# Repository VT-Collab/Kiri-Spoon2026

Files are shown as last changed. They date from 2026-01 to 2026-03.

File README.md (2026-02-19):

# Kiri-Spoon: A Kirigami Utensil for Robot-Assisted Feeding

Kiri-Spoon: A Kirigami Utensil for Robot-Assisted Feeding

There are three folders: Handheld Kirispoon, Robotic Kirispoon End-Effector, and Ansys Model

There are prt, zip, step, and md files in the Handheld Kirispoon and Robotic End-Effector folders

md files provide instructions for Kirispoon reproduction

Download the zip file for the assembly and all necessary files

Individual prt files are located in the folders

The same kirigami sheet is located in multiple folders

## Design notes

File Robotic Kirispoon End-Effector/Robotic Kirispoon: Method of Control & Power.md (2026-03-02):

# **Robotic Kirispoon: Method of Control & Power**

## Description
There are multiple ways to control and power the Robotic Kirispoon. This document gives the two examples of control that were utilized in research. This document includes materials, tools, and instructions to reproduce these methods of control. An order form is located at the end of each method. 

## Method 1: Control through the use of a button
This method involves wiring the robotic kirispoon to an adaptable power source, an arduino, and a button to open and close the end-effector. This can be useful when providing an easy interface for users.

### Parts
    - Power Adapter 7 volts
    - Push Button
    - Four 10K Ohm Resistors 
    - Robotic Kirispoon End-effector (Servo Motor)
    - Arduino
    - Arduino Cable (This is used to connect the Arduino to the computer)
    - 9 Male/Male Wires
    - DC barrel jack adapter (Enables the power supply to connect to the Servo Motor)
    - Half Breadboard

### Files
    - KiriButton.ino 

## Instructions



    1. Build the circuit shown above
        *Note: Pay attention to the specific pins on the Arduino and the specific wire colors on the Servo Motor
        *Note: The Servo Motor is a part of the Robotic Kirispoon End-effector
    2. Download the following files:
        *Kiributton.ino
    3. Connect the Arduino to the computer with the above file
    4. In the Arduino IDE, open the Kiributton.ino sketch
    5. Upload the sketch to the Arduino to run the code
    6. Turn on the power supply to the motor
    7. Pressing the button will move the motor to open and close the Robotic Kirispoon, completing method 1

## Order List for Method 1
There are multiple ways to make the circuit shown in Method 1. The parts list below will contain the items to make the circuit utilized during research. A picture of that circuit is included below. 
(Note: each resistor shown in the circuit diagram is 10k ohms)
ResearchCircuitArduino

Before clicking on the links in this list, there are a couple of important things to note:
    - Note: The Arduino Cable is for a USB type B, depending on the computer used, another cable may need to be selected
    - Note: This list assumes the Robotic Kirispoon is already built
    - Note: The left-most column shows the number of the units to order
    - Note: This list will yield more materials than necessary to build the circuit
    - Note: This list assumes that a printer is readily available
    - Note: The “Link Cost” column shows the price of the product in the link address when this document was made, 
            NOT the cost for the amount of material needed for one spoon

|# of Units|Part/Material|Unit Cost|
|---|---|---|
|1|[Arduino](https://store-usa.arduino.cc/products/arduino-uno-rev3?utm_source=google&utm_medium=cpc&utm_campaign=US-Pmax&gad_source=1&gad_campaignid=21317508903&gbraid=0AAAAACbEa84vFf-vMm0bSp7Ru9_hjazM2&gclid=CjwKCAiAmp3LBhAkEiwAJM2JUPkOYBex2DY1xz7MZbzy9ACP6xAJaNXNZbybs5sxCYbR4J5JAEu0iBoCLawQAvD_BwE )|$27.60|
|1|[Arduino Cable](https://store-usa.arduino.cc/collections/cables-wires/products/usb-2-0-cable-type-ab#looxReviews )|$6.50|
|1|[Power Adapter 7 volts  (includes a DC barrel jack adapter)](https://www.amazon.com/dp/B0B5GFJNS2/ref=sspa_dk_detail_3?psc=1&pd_rd_i=B0B5GFJNS2&pd_rd_w=mGGio&content-id=amzn1.sym.386c274b-4bfe-4421-9052-a1a56db557ab&pf_rd_p=386c274b-4bfe-4421-9052-a1a56db557ab&pf_rd_r=2W6D7QCPWHGRAN1Y680W&pd_rd_wg=op3lr&pd_rd_r=806a2af1-b4f9-48da-8165-049daf2cf8ef&sp_csd=d2lkZ2V0TmFtZT1zcF9kZXRhaWxfdGhlbWF0aWM )|$17.99|
|1|[10k Ohm Resistors (10 pack)](https://www.amazon.com/California-JOS-Carbon-Resistor-Tolerance/dp/B0BR68QQPF/ref=sr_1_3?dib=eyJ2IjoiMSJ9.CitfKyPFE5pIWUVS7QgFNKXsj0QNgNypSwtNjBlsotvRwHn9qigSDCFk9SjCPPLbGNeCPsj8pLYMNuQCzHIqfW5iafJLYPsvQ9Wtt7kOpD-ID9ATt-K7_nxSs8aBtOSvzfdjrLO01KDsecxBB8ocr0xEixn1dCMHj_CFr7BhUZ6v7vj1YpLuwfVmYQP2TTMp7lnIaGpZYiojs9D-rkrHKbrX4pLbe8gkUY-w42ecziI.BQNyUV8xU7tfTQWOo8j2iS77g3V_r7tXK5orqj6SgIE&dib_tag=se&hvadid=792677910694&hvdev=c&hvexpln=67&hvlocphy=9197701&hvnetw=g&hvocijid=18200258952104306485--&hvqmt=e&hvrand=18200258952104306485&hvtargid=kwd-6783760661&hydadcr=2794_13896043&keywords=10k%2Bohm%2Bresistor&mcid=4133edb7e5523276b60c85ef7beef09d&qid=1768418028&sr=8-3&th=1)|$3.99|
|1|[Half Breadboard](https://www.digikey.com/en/products/detail/dfrobot/FIT0096/7597069?gclsrc=aw.ds&gad_source=1&gad_campaignid=20232005509&gbraid=0AAAAADrbLliWzviSy71Vuvh3rn68vr0yy&gclid=CjwKCAiAmp3LBhAkEiwAJM2JUAsJKqjgIozuQ8PYXdKIrhqhSSRvO_wl6e72EOud3CsVuHPRZbkJcBoCjGIQAvD_BwE )|$2.90|
|1|[Push button (does not need an adapter)](https://www.amazon.com/EG-STARTS-Buttons-Illuminated-Machine/dp/B01LZMANZ7#:~:text=Wiring%20Information:,No%20lock%20button%20switch. )|$11.99|
|1|[M/M Wires (20 Count)](https://www.digikey.com/en/products/detail/sparkfun-electronics/PRT-12795/5993860)|$2.95|
||Total Cost: |$73.92|

## Method 2: Control through the use of Serial Messages
This method involves wiring the Robotic Kirispoon to an adaptable power source and Arduino. Serial messages will be received by the Arduino to open and close the end-effector. Researchers utilized VS Code to send Serial messages; an example is included. This can be useful when combining the open and close capability of the robotic Kirispoon with controls for other machines. An example of this would be using a controller to control the Robotic Kirispoon and the robot arm it is attached to.

### Parts
    - Power Adapter 7 volts
    - Robotic Kirispoon End-effector (Servo Motor)
    - Arduino
    - Arduino Cable (This is used to connect the Arduino to the computer)
    - 3 Male/Male Wires
    - Breadboard

### Files
    - Endeffector_Control_Example.ino
    - Open_close_Kirispoon.py

### Instructions


    1. Build the circuit shown above
        *Note: Pay attention to the specific pins on the Arduino and the specific wires on the Servo Motor
    2. Download the following files
        - Endeffector_Control_Example.ino
    3. Connect the Arduino to the computer with the above file
    4. In the Arduino IDE, open the Endeffector_Control_Example.ino sketch
    5. Upload the sketch to the Arduino to run the code
    6. Turn on the power supply to the motor
    7. In another software, such as Visual Studio, controlling the Robotic Kirispoon can be done by sending 
        the specific messages over the Arduino Cable, which correspond to the action in the Arduino code. 
        An example of sending serial messages in VS Code is seen in the Open_close_Kirispoon.py and below. 


    To run the example shown above, follow the steps below:
    1. Download the following:
        - Open_close_Kirispoon.py
    2. Open the file above in VS Code
    3. Go into the folder containing Open_close_Kirispoon.py
    4. Right click on any white space in the folder to open a menu
    5. Choose “Open in Terminal”
    6. Make sure all the dependencies in requirements.txt are downloaded
    7. Type the following in your terminal: 
        python Open_close_Kirispoon.py
    8. Press the "enter" key

## Order List for Method 2
There are multiple ways to make the circuit shown in Method 2. The parts list below will contain the items to make the circuit utilized during research. This circuit is similar to the one featured in the order form above, except that the orange and green wires, the button, and the resistors have been removed. A computer capable of sending serial messages corresponding to the Arduino is assumed to be available. 

Before clicking on the links in this list, there are a couple of important things to note:

    - Note: The Arduino Cable is for a USB type B. Depending on the computer used, another cable may need to be selected
    - Note: This list assumes the Robotic Kirispoon is already built
    - Note: The left-most column shows the number of the material to order
    - Note: This list will yield more materials than necessary to build the circuit
    - Note: This list assumes that a printer is readily available
    - Note: This list assumes that a computer or other hardware device capable of sending serial messages is readily available
    - Note: The “Link Cost” column shows the price of the product in the link address when this document was made, 
            NOT the cost for the amount of material needed for one spoon

|# of Units|Part/Material|Unit Cost|
|---|---|---|
|1|[Arduino](https://store-usa.arduino.cc/products/arduino-uno-rev3?utm_source=google&utm_medium=cpc&utm_campaign=US-Pmax&gad_source=1&gad_campaignid=21317508903&gbraid=0AAAAACbEa84vFf-vMm0bSp7Ru9_hjazM2&gclid=CjwKCAiAmp3LBhAkEiwAJM2JUPkOYBex2DY1xz7MZbzy9ACP6xAJaNXNZbybs5sxCYbR4J5JAEu0iBoCLawQAvD_BwE )|$27.60|
|1|[Arduino Cable](https://store-usa.arduino.cc/collections/cables-wires/products/usb-2-0-cable-type-ab#looxReviews )|$6.50|
|1|[Power Adapter 7 volts (includes a DC barrel jack adapter)](https://www.amazon.com/dp/B0B5GFJNS2/ref=sspa_dk_detail_3?psc=1&pd_rd_i=B0B5GFJNS2&pd_rd_w=mGGio&content-id=amzn1.sym.386c274b-4bfe-4421-9052-a1a56db557ab&pf_rd_p=386c274b-4bfe-4421-9052-a1a56db557ab&pf_rd_r=2W6D7QCPWHGRAN1Y680W&pd_rd_wg=op3lr&pd_rd_r=806a2af1-b4f9-48da-8165-049daf2cf8ef&sp_csd=d2lkZ2V0TmFtZT1zcF9kZXRhaWxfdGhlbWF0aWM )|$17.99|
|1|[Half Breadboard](https://www.digikey.com/en/products/detail/dfrobot/FIT0096/7597069?gclsrc=aw.ds&gad_source=1&gad_campaignid=20232005509&gbraid=0AAAAADrbLliWzviSy71Vuvh3rn68vr0yy&gclid=CjwKCAiAmp3LBhAkEiwAJM2JUAsJKqjgIozuQ8PYXdKIrhqhSSRvO_wl6e72EOud3CsVuHPRZbkJcBoCjGIQAvD_BwE )|$2.90|
|1|[M/M Wires (20 Count)](https://www.digikey.com/en/products/detail/sparkfun-electronics/PRT-12795/5993860 )|$2.95|
||Total Cost: |$57.94|

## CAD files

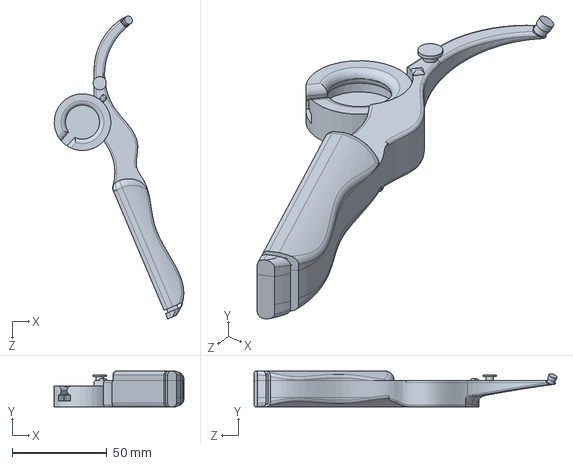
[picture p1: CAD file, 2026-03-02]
Handheld Kirispoon/Part Files/RightHandle.SLDPRT
68.5 x 19.0 x 160.1 mm

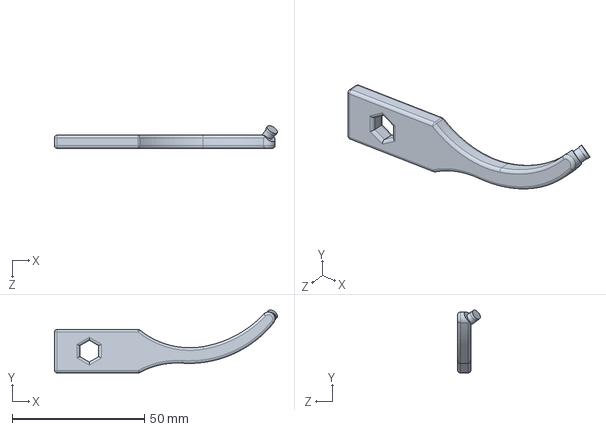
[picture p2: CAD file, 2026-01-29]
Robotic Kirispoon End-Effector/Part Files/Angled_Kiripost_45Right.SLDPRT
84.4 x 23.8 x 8.60 mm

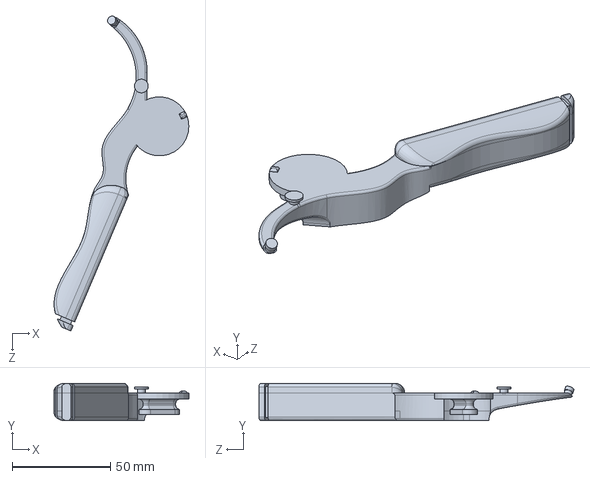
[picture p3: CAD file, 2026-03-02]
Handheld Kirispoon/Part Files/LeftHandle.SLDPRT
68.5 x 19.0 x 160.1 mm

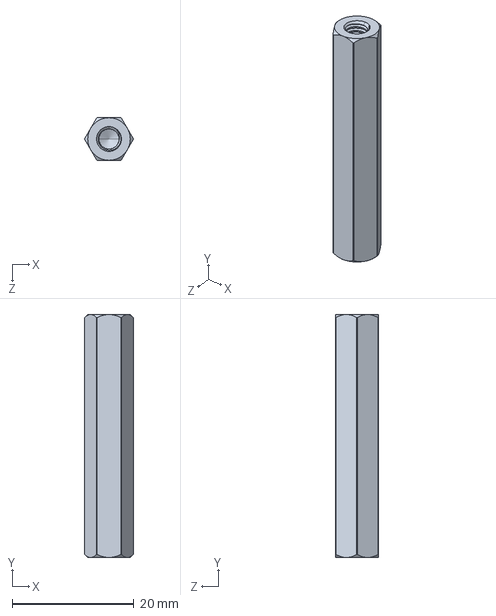
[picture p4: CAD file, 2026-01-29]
Robotic Kirispoon End-Effector/Part Files/HexShaft.SLDPRT
8.00 x 40.0 x 7.00 mm

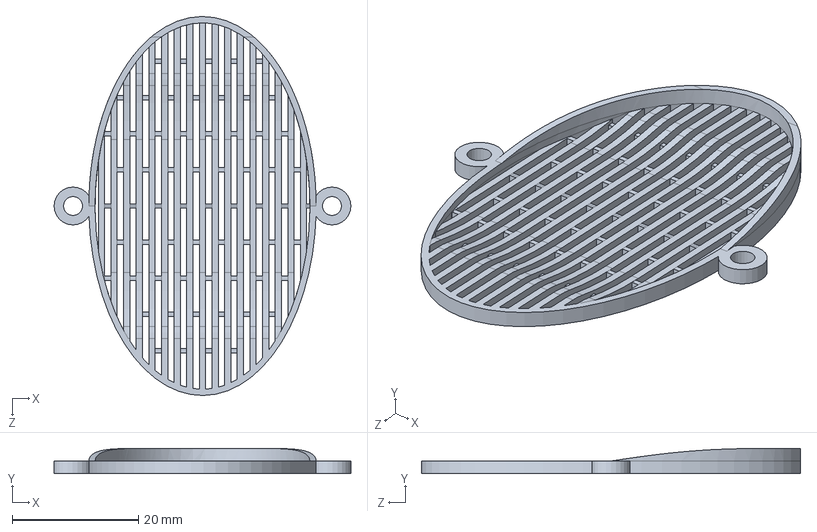
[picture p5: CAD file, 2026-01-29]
Handheld Kirispoon/Part Files/KirigamiMesh.SLDPRT
47.0 x 4.00 x 60.0 mm

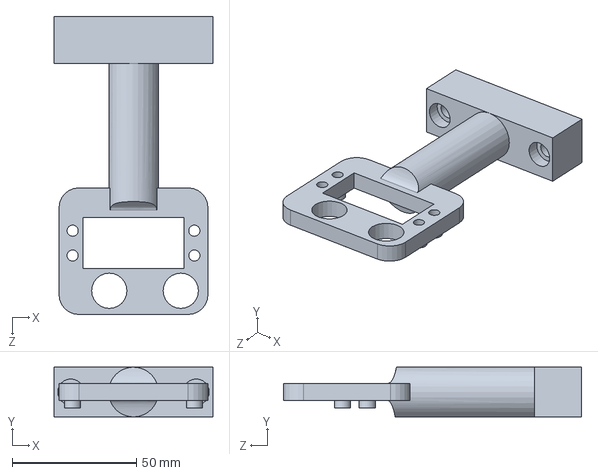
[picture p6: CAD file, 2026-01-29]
Robotic Kirispoon End-Effector/Part Files/PandaHousingOneServo.SLDPRT
64.0 x 20.0 x 120.0 mm

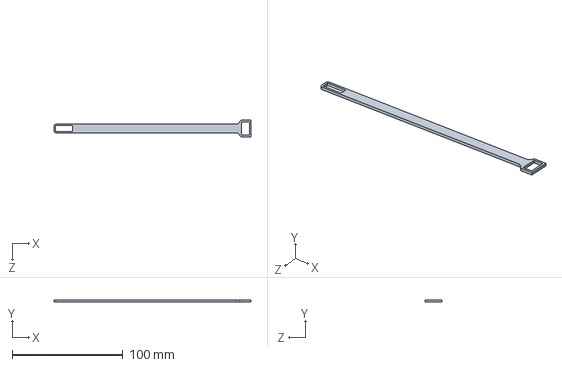
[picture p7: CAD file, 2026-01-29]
Handheld Kirispoon/Part Files/GoodieStrap.SLDPRT
178.0 x 2.00 x 15.0 mm

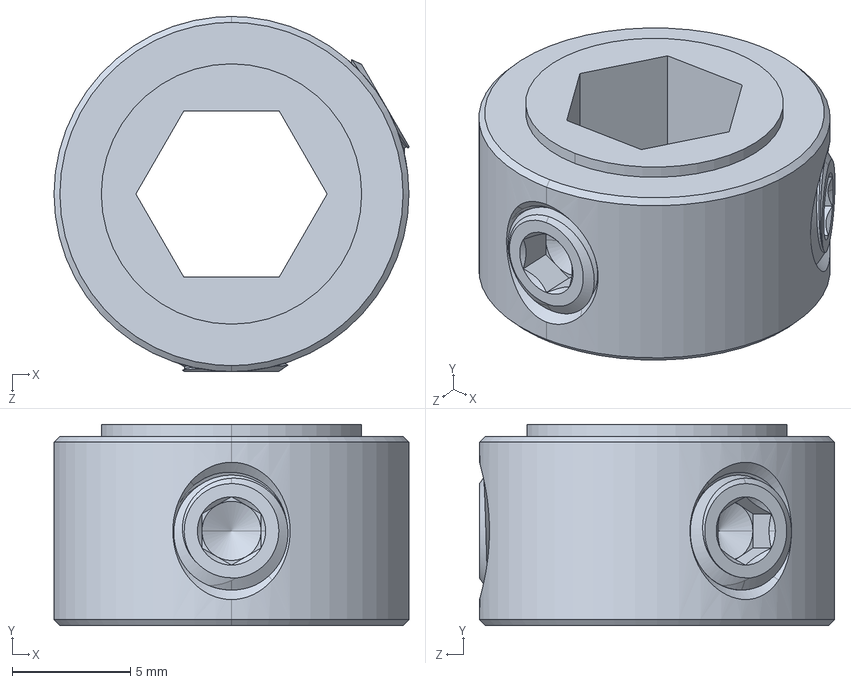
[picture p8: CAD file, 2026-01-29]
Robotic Kirispoon End-Effector/Part Files/HexCollar.SLDPRT
15.0 x 8.50 x 15.0 mm

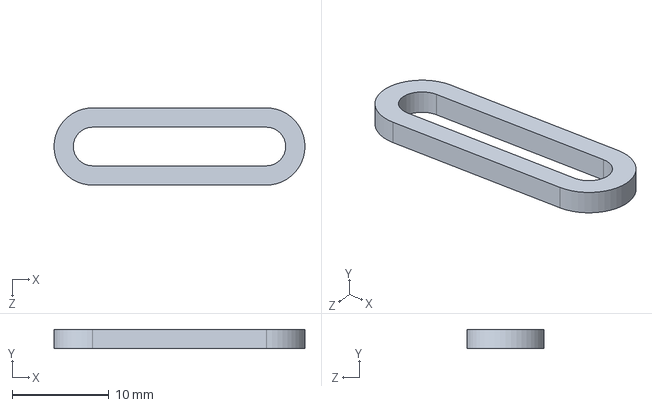
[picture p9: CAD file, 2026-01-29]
Handheld Kirispoon/Part Files/TPU Band.SLDPRT
26.0 x 2.00 x 8.00 mm

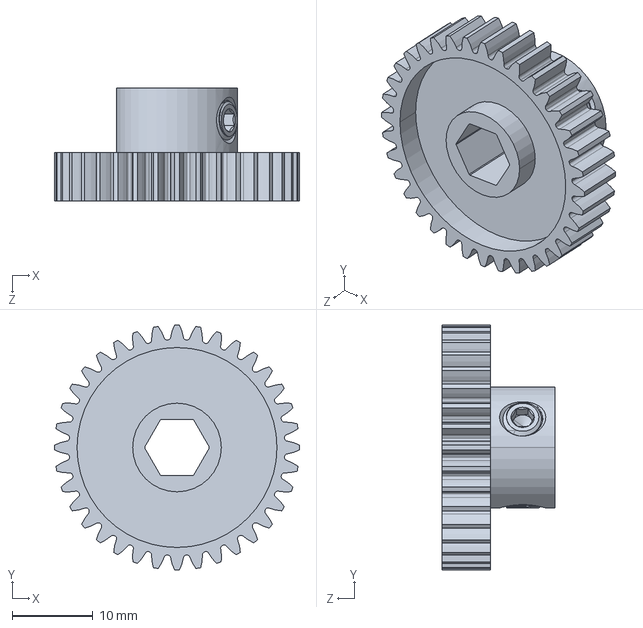
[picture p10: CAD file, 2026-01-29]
Robotic Kirispoon End-Effector/Part Files/HexGear36T.SLDPRT
30.4 x 30.4 x 14.0 mm

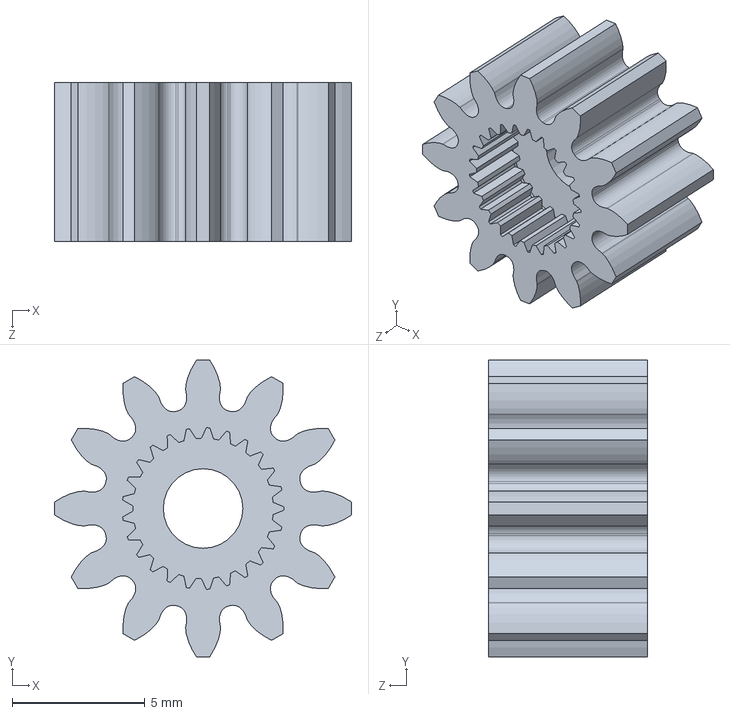
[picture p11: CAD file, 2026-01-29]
Robotic Kirispoon End-Effector/Part Files/ServoGear.SLDPRT
11.2 x 11.2 x 6.00 mm

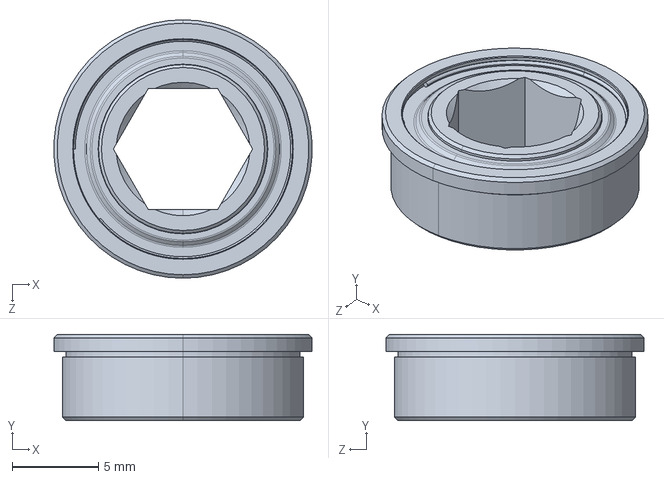
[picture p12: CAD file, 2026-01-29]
Robotic Kirispoon End-Effector/Part Files/HexBearing.SLDPRT
15.0 x 5.00 x 15.0 mm

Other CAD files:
Robotic Kirispoon End-Effector/Part Files/Angled_Kiripost_45Left.SLDPRT
Handheld Kirispoon/STL Files/GoodieStrap.STL
Handheld Kirispoon/STL Files/KirigamiMesh.STL
Handheld Kirispoon/STL Files/LeftHandle.STL
Handheld Kirispoon/STL Files/RightHandle.STL
Handheld Kirispoon/STL Files/TPU Band.STL
Robotic Kirispoon End-Effector/STL Files/KirigamiMesh.STL
Robotic Kirispoon End-Effector/STL Files/PandaHousingOneServo.STL

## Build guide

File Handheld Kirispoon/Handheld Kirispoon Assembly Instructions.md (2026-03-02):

# **Handheld Kirispoon Assembly Instructions**

## Description

The Handheld Kirispoon is a 3D-printed assistive device that functions by encompassing food with a flexible mesh. This document includes materials, tools, and instructions to reproduce the device. An order form is located at the end of this document.

### Materials
- PLA 3D-printing filament (35 grams)
- TPU (85A) 3D-printing filament (8 grams)

### Tools
- 3D printer
- Pliers (See Note in Step 2)

### Files
- LeftHandle.STL
- RightHandle.STL
- TPU Band.STL
- KirigamiMesh.STL
- GoodieStrap.STL (Optional)

## Instructions

#### 1. Download the following .STL files:
    - LeftHandle.STL
    - RightHandle.STL
#### 2. Print PLA parts

    1. On a 3D printing software, import the two files downloaded in step 1
    
handlesOnPrinterBed
    
    2. Orient the two files onto the printer bed as shown above
    3. Adjust the printer settings to allow PLA printing
    4. Load PLA filament into the 3D printer
    5. Upload and print the two PLA parts
    6. Take the two parts off and remove the supports
        *A small pair of pliers makes removing the supports easier
#### 3. Download the following .STL files:
    - TPU Band.STL
    - KirigamiMesh.STL
    - GoodieStrap.STL (Optional)
#### 4. Print TPU parts
    1. On a 3D printing software, import the files downloaded in step 3



    2. Orient the files onto the printer bed as shown above
    3. Adjust the printer settings to allow TPU printing
        *Note: Some printers have trouble printing TPU. Look up the best parameters for printing TPU filament on your printer.
    4. Load TPU filament into the 3D printer
    5. Upload and print the TPU parts
#### 5. Assemble



    1. Connect the two handles by aligning the two bumps located in circles in Figure (a). Imagine a line between the two bumps. 
        Orient that line so it passes through the opening in the right handle. Slide the bumps toward each other in a straight line 
        so that the left handle slides into the right handle. The handles should now rotate while staying connected, similar to 
        a pair of pliers
    2. Take the kirigami sheet and locate the two circular holes on the side. Orient the kirigami sheet so that the thicker part 
        is closer to the handles. Attach the circular holes of the kirigami sheet to the pegs on the end of the handles. 
        These pegs can be seen in the red circles of Figure (b). The attachment will be a tight fit, but this will ensure that 
        the kirigami sheet is snug on the handles. At this point, squeezing the handles will stretch the kirigami sheet. 
    3. Wrap the TPU band around the two remaining pegs. These pegs are in the red circles of Figure (c). The band helps the handles 
        spring back by adding some resistance to the handles when they are squeezed. 
    4. There should now be a fully assembled Kirispoon similar to this one shown in Figure (d).
     
    - Optional Step: If the user would like some assistance holding the Kirispoon, the goodie strap can be installed on the 
        opposite handle of the user's dominant hand. If the user is right handed, then the goodie strap would go on the 
        left handle and vice versa. Starting from the bottom, slide the “thicker” hole of the goodie strap past the “thick” 
        part of the handles. Then slide the remaining hole into the grooves at the bottom of the handle.

## Order List
Before clicking on the links in this list, there are some important things to note:

    - The two filament spools below contain enough filament for several spoons
    - This list assumes that a printer is readily available
    - The specific links listed below are the materials utilized in the Kirispoon research study; 
            it is possible to find the listed materials from other sources
    - The “Roll Cost” column shows the price of the product in the link address when this document was made, 
            NOT the cost for the amount of material needed for one spoon

|Material|g per Roll|Roll Cost|g per Kirispoon|Kirispoon Cost|
|---|---|---|---|---|
|[PLA filament(any color)](https://us.store.bambulab.com/products/pla-basic-filament?srsltid=AfmBOoo7uD4aZrYHzutCN6MeIgpNWLYGZYQ993Mq-DI3_bWOmJg2ZiCG&id=43045599215752)|1000g|$19.99|35g|$0.70|
|[TPU 85A filament](http://matterhackers.com/store/l/ninjatek-ninjaflex-tpu-filament/sk/MV0S1W9G?rcode=PMAX_GENPOPFIL&gad_source=1&gad_campaignid=20511284107&gbraid=0AAAAADtQ4S2UubuybuOmpFmA1j5LN21QE&gclid=CjwKCAiA95fLBhBPEiwATXUsxMzSsgJE8i6oHTvo0HaZhD9AmPCctGVFT8BKvup_QHG0nufGQGCBKRoCVewQAvD_BwE)|500g|$54.25|8g|$0.87|
|Total:|1500g|$74.24|43g|$1.57|

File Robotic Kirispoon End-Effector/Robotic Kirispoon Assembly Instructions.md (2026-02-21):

# **Robotic Kirispoon Assembly Instructions**
## Description

The Robotic Kirispoon End-Effector is a device developed to securely grab food while maintaining an ergonomic shape for the user's mouth. This document includes materials, tools, and instructions to reproduce the device. An order form is located at the end of this document. 

### Materials
- PLA 3D-printing filament (40 grams)
- TPU 85A 3D-printing filament (5 grams)

### Tools
- Screw Driver
- Allen Wrench 2.5mm

### Parts
- 2305 Series Brass, MOD 0.8, Servo Gear (25 Tooth Spline, 12 Tooth) [Quantity:1]
- 2303 Series Steel, MOD 0.8 Pinion Gear (8mm REX Bore, 36 Tooth) [Quantity:2]
- 1611 Series Flanged Ball Bearing (8mm REX ID x 14mm OD, 5mm Thickness) [Quantity:2]
- 2920 Series Steel Set-Screw Collar (8mm REX Bore) [Quantity:4]
- 1516 Series 8mm REX Standoff (M4 x 0.7mm Threads, 40mm Length) [Quantity:2] 
- 2000 Series Dual Mode Servo (25-2, Torque) [Quantity:1]
- Screws (M4, Length 16mm) [Quantity:3]
- Nuts (M4) [Quantity:3]

### Files
- Angled_Kiripost_45Left.STL
- Angled_Kiripost_45Right.STL
- PandaHousingOneServo.STL
- KirigamiMesh.STL

## Preparation
#### 1. Download the following .STL files:
    - Angled_Kiripost_45Left.STL
    - Angled_Kiripost_45Right.STL
    - PandaHousingOneServo.STL

#### 2. Print PLA Parts
    1. On a 3D printing software, import the three files downloaded in step 1
    


    2. Orient the three files onto the printer bed as shown above
    3. Adjust the printer settings to allow PLA printing
    4. Load PLA filament into the 3D printer
    5. Upload and print the two PLA parts
    6. Take the three parts off and remove the supports
        *A small pair of pliers makes removing the supports easier
#### 3. Download the following .STL file:
    - KirigamiMesh.STL
#### 4. Print the TPU part
    1. In a 3D printing software, import the file downloaded in step 3
    

    
    2. Orient the files onto the printer bed as shown above
    3. Adjust the printer settings to allow TPU printing
        *Note: Some printers have trouble printing TPU. Look up the best parameters for printing TPU filament on your printer. 
    4. Load TPU filament into the 3D printer
    5. Upload and print the TPU parts
    6. Move to the Assembly instructions while printing

## Assembly



1. Orient the servo motor onto the Panda housing as shown above. Use three screws and nuts to secure the servo to the housing. The nuts should be flush against the housing.



2. Insert the ball bearings as shown in the figure above. These should push into the housing and be held in place by friction.



3. Slide a REX standoff into each of the ball bearings. Secure the REX standoffs by installing collars on the side of the standoffs closest to the servo motor, as shown above. The collar can be fastened with the Allen wrench until it no longer moves when little force is applied. Do not over-tighten the collar; this will damage the REX standoffs. 



4. Place the servo gear onto the servo motor. Then slide the 36-tooth gears onto the REX standoffs as shown above.



5. Press the Angled Kiriposts onto the REX standoffs while paying careful attention to the orientation as shown above. The Kiriposts are designed for a tight fit, so this step will take some force.



6. Fasten a collar on the bottom of each standoff as shown above.



7. Once the Kirigami sheet is done printing, remove it from the printer. There are two circular holes on the kirigami sheet that will fit onto the pegs located on the end of each Kiripost. The thicker part of the kirigami sheet should be closest to the servo motor, as shown above.



8. The assembly should now be complete as shown above. 

## Controlling and Powering the Robotic Kirispoon
Once the Robotic Kirispoon has been assembled, the next step is to figure out a method of power and control. Look at the **“Robotic Kirispoon: Method of Control & Power”**
document for examples on how to control and power the end-effector.

## Order List
Before clicking on the links in this list, there are some things to note:

    - Note: The left-most column shows the amount of material/parts needed for one spoon
    - Note: The two filament spools below contain enough filament for several spoons
    - Note: This list assumes that a printer is readily available
    - Note: The specific links listed below are the materials utilized in the Kirispoon research study; 
            it is possible to find the listed materials from other sources
    - Note: The “Link Cost” column shows the price of the product in the link address when this document was made, 
            NOT the cost for the amount of material needed for one spoon

**Total 3D-Printing Filament Cost**
|Material|g per Roll|Roll Cost|g per End-Effector|End-Effector Cost|
|---|---|---|---|---|
|[PLA filament(any color)](https://us.store.bambulab.com/products/pla-basic-filament?srsltid=AfmBOoo7uD4aZrYHzutCN6MeIgpNWLYGZYQ993Mq-DI3_bWOmJg2ZiCG&id=43045599215752)|1000g|$19.99|40g|$0.80|
|[TPU 85A filament](http://matterhackers.com/store/l/ninjatek-ninjaflex-tpu-filament/sk/MV0S1W9G?rcode=PMAX_GENPOPFIL&gad_source=1&gad_campaignid=20511284107&gbraid=0AAAAADtQ4S2UubuybuOmpFmA1j5LN21QE&gclid=CjwKCAiA95fLBhBPEiwATXUsxMzSsgJE8i6oHTvo0HaZhD9AmPCctGVFT8BKvup_QHG0nufGQGCBKRoCVewQAvD_BwE)|500g|$54.25|5g|$0.55|
|Total:|1500g|$74.24|45g|$1.35|

**Total Part Cost**
<table>
  <tr>
    <th># of Units</th>
    <th>Part/Material</th>
    <th>Unit Cost</th>
    <th>Cost</th>
  </tr>

  <tr>
    <td>1</td>
    <td><a href="https://www.gobilda.com/2000-series-dual-mode-servo-25-2-torque/">2000 Series Dual Mode Servo (25-2, Torque)</a></td>
    <td>$36.99</td>
    <td>$36.99</td>
  </tr>

  <tr>
    <td>1</td>
    <td><a href="https://www.gobilda.com/2305-series-brass-mod-0-8-servo-gear-25-tooth-spline-12-tooth/">2305 Series Brass, MOD 0.8, Servo Gear (25 Tooth Spline, 12 Tooth)</a></td>
    <td>$8.99</td>
    <td>$8.99</td>
  </tr>

  <tr>
    <td>2</td>
    <td><a href="https://www.gobilda.com/2303-series-steel-mod-0-8-pinion-gear-8mm-rex-bore-36-tooth/">2303 Series Steel, MOD 0.8 Pinion Gear (8mm REX Bore, 36 Tooth)</a></td>
    <td>$12.59</td>
    <td>$25.18</td>
  </tr>

  <tr>
    <td>1</td>
    <td><a href="https://www.gobilda.com/1611-series-flanged-ball-bearing-8mm-rex-id-x-14mm-od-5mm-thickness-2-pack/">1611 Series Flanged Ball Bearing (8mm REX ID x 14mm OD, 5mm Thickness) (2 Pack)</a></td>
    <td>$5.99</td>
    <td>$5.99</td>
  </tr>

  <tr>
    <td>2</td>
    <td><a href="https://www.gobilda.com/2920-series-steel-set-screw-collar-8mm-rex-bore-2-pack/">2920 Series Steel Set-Screw Collar (8mm REX Bore) (2 Pack)</a></td>
    <td>$5.99</td>
    <td>$11.98</td>
  </tr>

  <tr>
    <td>1</td>
    <td><a href="https://www.gobilda.com/1516-series-8mm-rex-standoff-m4-x-0-7mm-threads-40mm-length-4-pack/">1516 Series 8mm REX Standoff (M4 x 0.7mm Threads, 40mm Length) (4 Pack)</a></td>
    <td>$5.29</td>
    <td>$5.29</td>
  </tr>

  <tr>
    <td>1</td>
    <td><a href="https://www.gobilda.com/m4-x-0-7mm-zinc-plated-socket-head-screw-16mm-length/?sku=2800-0004-0016">Screws (M4, Length 16mm) (25 Pack)</a></td>
    <td>$3.79</td>
    <td>$3.79</td>
  </tr>

  <tr>
    <td>1</td>
    <td><a href="https://www.gobilda.com/m4-x-0-7mm-nylock-nut/?sku=2812-0004-0007">Nuts (M4) (25 Pack)</a></td>
    <td>$2.99</td>
    <td>$2.99</td>
  </tr>

  <tr>
    <td colspan="3">Total:</td>
    <td>$101.20</td>
  </tr>
</table>

**Total Cost of One Robotic End-Effector**
||3D-Printing Filament|Parts|Summed Total|
|---|---|---|---|
|Total Cost: |$1.35|$101.20|**$102.55**|

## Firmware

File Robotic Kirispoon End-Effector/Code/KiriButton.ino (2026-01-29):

// KiriButton Code
/* Created by Keone Leao

  Description: This code was created to control the robotic
  kirispoon end effector with only a button. 
  This program will print what state the kirigami is in
  as well as open and close the kirigami. The 
  "openPosition" and "closedPosition" variables can
  be changed to stretch and compress the kirigami different
  amounts. 
  ~ to see the Serial.print() messages, go to 'Tools' 
    and press 'Serial Monitor'. Or press Ctrl+Shft+M.
  ~ fastest way to clear the serial monitor is to close 
    and open again*/


#include <Servo.h> // Include the Servo library

Servo myservo; // Create a servo object to control a servo (MAX 7.4 V)
               // ~voltage can be less if less torque is required~
int KiriState = 0; // 0 closed, 1 open
const int buttonPin = 2; // arduino pin the button is wired to
const int openPosition = 50; // position of servo when kirigami is open
const int closedPosition = 5; // position of servo when kirigami is closed

void setup() {
  myservo.attach(9); // Attaches the servo on pin 9 to the servo object
  myservo.write(openPosition); // start with kirispoon open
  pinMode(buttonPin, INPUT_PULLUP); // specifies how to interpret the button
  Serial.begin(9600); // baud rate
  Serial.print("Begin"); // tells user when loop is about to begin
                     // You can change '9' to the digital pin your servo's signal wire is connected to
}

void loop() {
  int buttonState = digitalRead(buttonPin); // reads if the button is pressed
  //Serial.print(buttonState);
  if (buttonState == HIGH) // button pressed
  {
    Serial.print("pressed");

    if (KiriState == 0) // if kirigami is closed, then open it
    {
      KiriState = 1; // change kirigami state to open
      myservo.write(openPosition); // move servos to open
      Serial.print("open  ");
      delay(100); // short delay is needed for button signal to come through
    }
    else // else if kirigami is open, close it
    {
      KiriState = 0; // set kirigami state to closed
      myservo.write(closedPosition); // move servo to close kirigami
      Serial.print("closed  ");
      delay(100); // short delay is needed for button signal to come through
    }
  }

  delay(200); // delay is needed so one button press does not do two actions
}

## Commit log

2026-01-29 Updated handheld and robotic folder, Got rid of Kirispoon 2024 folder
    [Angled_Kiripost_45Left.SLDPRT, Angled_Kiripost_45Right.SLDPRT, GoodieStrap.SLDPRT, GoodieStrap.STL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]
2026-01-29 Update and rename Robotic Kirispoon Assembly Instructions to Robotic Kirispoon Assembly Instructions.md
2026-01-29 Update Handheld Kirispoon Assembly Instructions.md
2026-01-30 Update Robotic Kirispoon Assembly Instructions.md
2026-01-30 Update and rename Robotic Kirispoon: Method of Control & Power to Robotic Kirispoon: Method of Control & Power.md
2026-01-30 Update Robotic Kirispoon: Method of Control & Power.md
2026-02-19 Update Handheld Kirispoon Assembly Instructions.md
    adjusted the table at the bottom
2026-02-19 Update Handheld Kirispoon Assembly Instructions.md
    added filament cost per kirispoon
2026-02-19 Update Handheld Kirispoon Assembly Instructions.md
    fixed a format error
2026-02-21 split the part list into two different list. One has the same parts, the other is just for printing filaments, so we can see the cost for the amount of filament we are using
2026-02-21 fixed formating and some words in Robotic Kirispoon Assembly Instructions.md
2026-02-21 Update Robotic Kirispoon Assembly Instructions to be more clear in parts table.md
2026-03-02 Completed the example code instructions in Update Robotic Kirispoon: Method of Control & Power.md
2026-03-02 Uploaded the correct handle files
    The last files were slightly off, so I deleted them and added in these correct ones
    [LeftHandle.SLDPRT, RightHandle.SLDPRT]
2026-03-02 Uploaded the correct handle STL files
    The other STL files were incorrect so I deleted them, and uploaded these correct ones
    [LeftHandle.STL, RightHandle.STL]
2026-03-02 Update Handheld Kirispoon Assembly Instructions.md
    got rid of a comment that was just for me
2026-03-02 Added Correct Assembly.zip file
    Since the old handles were in the old assembly file, I had to delete the assembly file and upload this new one
